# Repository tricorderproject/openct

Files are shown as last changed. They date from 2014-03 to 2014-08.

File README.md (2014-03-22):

openct
======

Open Source Computed Tomography (CT) Scanner <br>
http://www.tricorderproject.org/openct <br>
Copyright (C) 2014  Peter Jansen and the Tricorder project <br>
peter@tricorderproject.org <br>

*Early alpha release v0.1*

# Introduction

The Open Source Computed Tomography (CT) Scanner project aims to move towards creating an inexpensive and open desktop computed tomography scanner for academic and educational purposes.  The most common form of computed tomography is radiographic using x-rays or gamma rays, although it is my hope that this project can serve as a general platform for other kinds of tomographic research with other, safer wavelengths. 

This project is intended for use with radioisotope "check" sources that are many orders of magnitude less intense than sources in a commercial or medical radiographic setups.  This means that even very low resolution images will take hours of measurement and integration time to assemble, and the resolution and signal to noise ratio of a scan are largely a function of time (and patience).  Much of the spirit of this project is to move towards creating better scans through the use of clever signal processing techniques or wavelengths that can be more efficiently detected, rather than increasing source intensity. 

# Open Source

This project is open hardware and is released under various open licenses.  Please see LICENSES.TXT for details.

For potential contributors, a list of suggested contributions and next steps can be found in TODO.TXT .

# Warning

This project has a variety of dangers associated with it, including (without limitation) its assembly and use.  This generally includes the typical hazards involved with assembling, testing, and using electronics projects, CNC projects, as well as using hand tools, power tools, and CNC manufacturing tools such as laser cutters or CNC routers.  This is not a first project in any of these areas, and one should be well experienced and comfortable in all aspects of this project's design, assembly, and use. 

In addition, for radiography this project makes use of a low intensity sealed radioactive radioisotope source.  You should be experienced and extremely comfortable with handling and using radioactive sources, understanding the potential dangers (and how to minimize them), as well as any local laws or regulations regarding such material.  Having advanced training in medical imaging, radiography, and/or radiation biophysics is highly recommended.  

In no case should any living thing be placed inside of or be scanned by the device. 

**DISCLAIMER OF WARRANTIES AND LIMITATION OF LIABILITY.**

UNLESS OTHERWISE SEPARATELY UNDERTAKEN BY THE LICENSOR, TO THE EXTENT POSSIBLE, THE LICENSOR OFFERS THE LICENSED MATERIAL AS-IS AND AS-AVAILABLE, AND MAKES NO REPRESENTATIONS OR WARRANTIES OF ANY KIND CONCERNING THE LICENSED MATERIAL, WHETHER EXPRESS, IMPLIED, STATUTORY, OR OTHER. THIS INCLUDES, WITHOUT LIMITATION, WARRANTIES OF TITLE, MERCHANTABILITY, FITNESS FOR A PARTICULAR PURPOSE, NON-INFRINGEMENT, ABSENCE OF LATENT OR OTHER DEFECTS, ACCURACY, OR THE PRESENCE OR ABSENCE OF ERRORS, WHETHER OR NOT KNOWN OR DISCOVERABLE. WHERE DISCLAIMERS OF WARRANTIES ARE NOT ALLOWED IN FULL OR IN PART, THIS DISCLAIMER MAY NOT APPLY TO YOU.

TO THE EXTENT POSSIBLE, IN NO EVENT WILL THE LICENSOR BE LIABLE TO YOU ON ANY LEGAL THEORY (INCLUDING, WITHOUT LIMITATION, NEGLIGENCE) OR OTHERWISE FOR ANY DIRECT, SPECIAL, INDIRECT, INCIDENTAL, CONSEQUENTIAL, PUNITIVE, EXEMPLARY, OR OTHER LOSSES, COSTS, EXPENSES, OR DAMAGES ARISING OUT OF THIS PUBLIC LICENSE OR USE OF THE LICENSED MATERIAL, EVEN IF THE LICENSOR HAS BEEN ADVISED OF THE POSSIBILITY OF SUCH LOSSES, COSTS, EXPENSES, OR DAMAGES. WHERE A LIMITATION OF LIABILITY IS NOT ALLOWED IN FULL OR IN PART, THIS LIMITATION MAY NOT APPLY TO YOU.

THE DISCLAIMER OF WARRANTIES AND LIMITATION OF LIABILITY PROVIDED ABOVE SHALL BE INTERPRETED IN A MANNER THAT, TO THE EXTENT POSSIBLE, MOST CLOSELY APPROXIMATES AN ABSOLUTE DISCLAIMER AND WAIVER OF ALL LIABILITY.

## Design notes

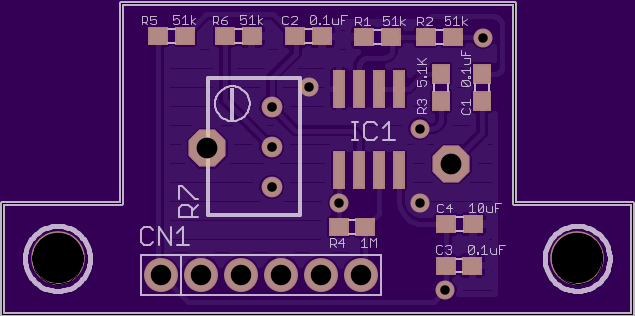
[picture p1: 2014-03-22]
pcb/external_comparator/type5comparator_top.png

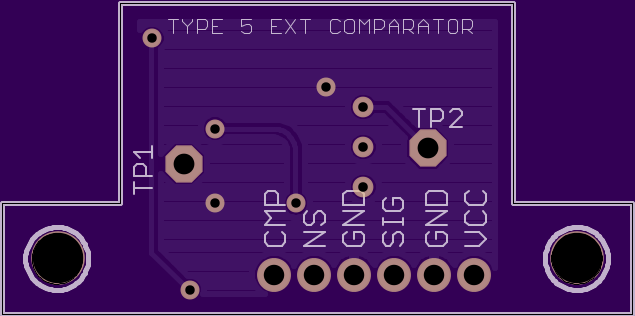
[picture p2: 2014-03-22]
pcb/external_comparator/type5comparator_bottom.png

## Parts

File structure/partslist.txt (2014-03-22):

========================
	GENERAL
========================

- T-slot captive nut holes are generally for 6/32 machine screws, 1/2 inch length. 
  A box of 100x 6/32 size 1/2 inch length bolts, nuts, and washers should suffice
  for most of the structural components.  A handful of longer lengths are required
  for the linear axis end plates and the carriage mounts. 

========================
	TABLE
========================

- MOTOR: NEMA14 5mm shaft [QTY: 1]
(Recommended: Japan Servo Co. Ltd. KP35FM2-035 from Sayal Electronics) 
(http://www.sayal.com)

- SCREW: M8 Nylon Screw and Nut.  [QTY: 1]
(Recommended: McMaster-Carr #98882A800, #93800A154)

- COUPLER: M5 to M8 Flex coupler
(Recommended: http://www.adafruit.com/products/1176 )

========================
	LINEAR AXES
========================

- MOTOR: NEMA14 5mm shaft [QTY: 2]
(Recommended: Japan Servo Co. Ltd. KP35FM2-035 from Sayal Electronics)

- BELT: At least 4 feet of 6mm width MLX (2.03mm pitch) belt.
(Recommended: Trim down SDP/SI (sdp-si.com) #A 6Z16MB89060 [QTY: 1])

- TIMING PULLEYS: SDP/SI (sdp-si.com) #A 6T16M018DF6005 [QTY: 2]

- IDLER PULLEYS: Makerslide Smooth Idler Wheel Kit [QTY: 2]
https://www.inventables.com/technologies/smooth-idler-wheel-kit
Also requires M5 bolts and lock nuts

- BUSHING: 1/4 Inner-diameter, 3/8 Outer-diameter snap bushing [QTY: 8]
(Recommended: from ACE Hardware)

- RODS: 1/4 aluminum rods, approx. 6 inches. [QTY: 4]
(Recommended: Cut from two 12 inch aluminum rods)

========================
	ROTATIONAL AXIS
========================

- MOTOR: NEMA17 5mm shaft [QTY: 1]
( Recommended: Adafruit http://www.adafruit.com/products/324 )

- BELT: SDP/SI (sdp-si.com) #A 6B16-115025 [QTY: 1]

- TIMING PULLEY: SDP/SI (sdp-si.com) #A 6T16M022DF6005 [QTY: 1]

========================
	BASE
========================

- BUSHING: 1/4 Inner-diameter, XX Outer-diameter, with flange
(Recommended: from ACE Hardware)

- RODS: 1/4 inch rods for timing gears, approx. 4 inches (cut to size) [QTY: 2]
(Recommended: Cut from one 12 inch aluminum rod)

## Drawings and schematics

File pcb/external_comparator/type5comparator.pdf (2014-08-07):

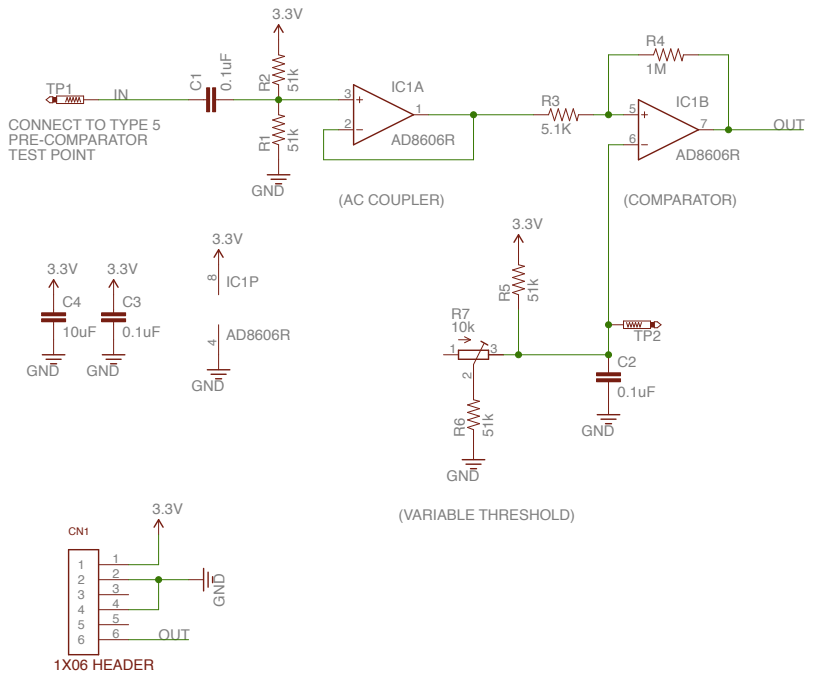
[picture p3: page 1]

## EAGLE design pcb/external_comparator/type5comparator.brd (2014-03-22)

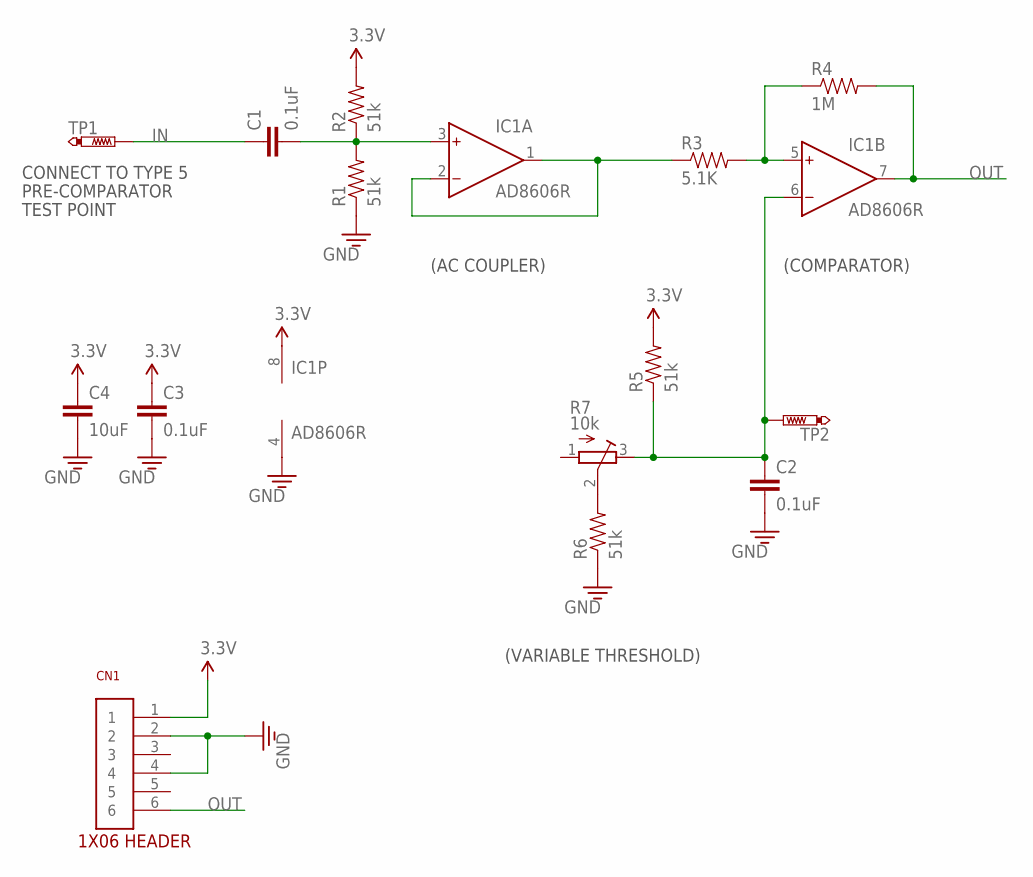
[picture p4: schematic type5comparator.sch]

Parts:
C1, C2, C3: 0.1uF; 0603
C4: 10uF; 0603
CN1: 1X06
IC1: AD8606R; SO8
R1, R2, R5, R6: 51k; 0603
R3: 5.1K; 0603
R4: 1M; 0603
R7: 10k; RTRIM3299W
TP1, TP2: PTR1PAD1-13; P1-13

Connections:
3.3V: C3.1, C4.1, CN1.1, IC1.8 (V+), R2.2, R5.2
GND: C2.2, C3.2, C4.2, CN1.2, CN1.4, IC1.4 (V-), R1.1, R6.1
IN: C1.1, TP1.TP
unnamed: R6.2, R7.2 (S)
unnamed: C1.2, IC1.3 (IN+), R1.2, R2.1
unnamed: IC1.1 (OUT), IC1.2 (IN-), R3.1
unnamed: IC1.5 (IN+), R3.2, R4.1
unnamed: C2.1, IC1.6 (IN-), R5.1, R7.3 (A), TP2.TP
OUT: CN1.6, IC1.7 (OUT), R4.2

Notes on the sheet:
(AC COUPLER)
(COMPARATOR)
(VARIABLE THRESHOLD)
CONNECT TO TYPE 5
PRE-COMPARATOR
TEST POINT

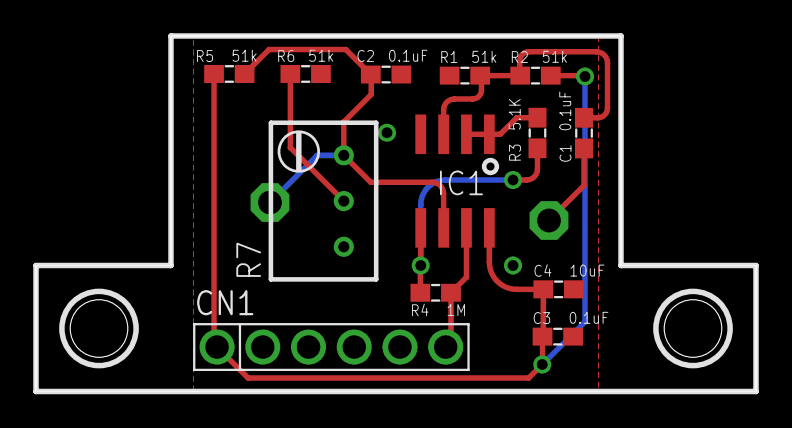
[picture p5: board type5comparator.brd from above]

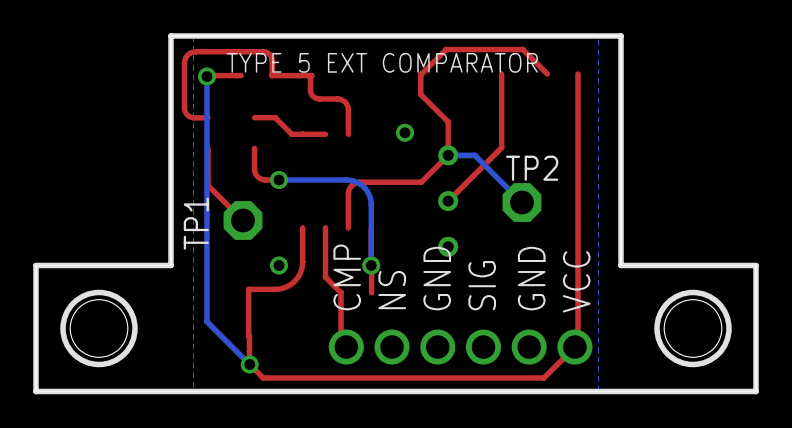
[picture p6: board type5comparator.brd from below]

Board: 2 copper layers, 40.0 x 19.8 mm, 15 parts (2 on the bottom side), 9 nets.

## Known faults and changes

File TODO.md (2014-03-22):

TODO LIST
======

Open Source Computed Tomography (CT) Scanner <br>
http://www.tricorderproject.org/openct <br>
Copyright (C) 2014  Peter Jansen and the Tricorder project <br>
peter@tricorderproject.org <br>

One of the most common questions an organizer of an open source project receives is, "How can I help?".  This TODO list outlines some of the near-term contributions that can be made to the project in a variety of categories, varying from simple to challenging. 

# Structural and Mechanical

- *End-stops:* Add end-stops ("limit switches") to each of the two linear axes, table axis, and rotational axis. 

- *Cabling:* Find a better solution to cable routing.  Cable routing is currently an issue, and there are a number of cables and signals that have to move from the rotating bore to the controller/arduino shield on the stationary base.  The rotational axis has to have at least 180&deg; of rotation, meaning that at one extreme it has a lot of slack, and at the other it has zero slack.  

- *Cabling, Part 2:* Is cabling the answer?  Should we turn the bore into a giant slip ring with two lines (+5V, GND) so that it can freely rotate 360&deg;, and wirelessly communicate between the bore and base using (for example) bluetooth? 

# Electronics

- *Arduino Shield:* Lay out an Arduino shield, for the latest Uno revision, that includes: (1) 4 Pololu stepper controllers (3 @ 5V, one selectable between 5V and 12V for the larger rotary axis stepper), (2) an SD/uSD socket for data storage, and (3) Headers/connectors for the end-stops, and an I2C accelerometer for sensing the rotational angle of the bore.  This should be compact enough to fit and mount inside one side of the base, and expose any required ports or connectors on the Arduino/Shield using clean cutouts in the back of the base. 

- *Rotational Sensing:* Currently the plan is to use an I2C accelerometer mounted in the bore as an absolute rotational sensor to sense the current angle of the bore.  Create the board for this, and add the supporting code into to the Arduino sketch.  A sensible place for this might be a tiny board that securely mounts on the back of the carriages and combines an accelerometer and two limit switches.  

# Source and Detector

- *Parallel Detector:* The current source/detector system is basically a working model of the first generation of CT scanner, that makes use of a single source and detector that are linearly scanned across the sample.  Modern systems speed this up dramatically by parallelizing the problem and using an large array of detectors in place of a single detector -- removing the need for linear scanning stages inside the bore, and reducing scan time by measuring all points for a given angle simultaneously.  This is a fairly large undertaking, and would likely require developing a custom parallel detector array with tens of detectors as inexpensively as possible.  

- *Alternate Sources/Detectors:* Using your advanced knowledge of optics, develop alternate source/detector pairs that examine different, safer wavelengths that objects of interest tend to be semi-transparent at.  (possible examples: Terahertz? Radio waves? Infrared?)

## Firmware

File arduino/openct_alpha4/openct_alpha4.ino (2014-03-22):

/*
  Open Source Computed Tomography (CT) Scanner 
  Demonstration code -- Early release alpha state

  This code is intended to demonstrate the basic functionality of the Open Source CT scanner, and 
  verify the basic functionality of the motion and detction system. 
  
  This code is intended for pairing with:
  1) An Arduino Uno R3
  2) A shield containing at least 3 (but preferably 4) Pololu stepper drivers
  3) A shield containing an SD card socket for data storage (the data is also mirrored over the serial console)
  4) A Radiation Watch Type 5 high energy particle detector modified with the external high-sensitivity comparator board
  5) The Open Source CT 4-axis motion system
  
  This code is in an prototype alpha state, and is intended for demonstration purposes only.  
  Portions of this file are from the Radiation Watch Type 5 Arduino example code.  All 
  other portions are released under the GPL V3 license. 
  
  TODO: 
  - Add 4 axis control as soon as the official 4-axis stepper shield is complete 
    (currently my prototype shield only has room for 3 stepper controllers, so either the table or rotational axis is disabled)
  - Add end-stop support for homing all axes
  - Add accelerometer for absolute angle sensing for rotational axis
  
 */
 
#include <SPI.h>
#include <SD.h>
const int SD_CS  = 10;    // Chip select pin of SD card
 
int TYPE5_DETECTOR = 2;   // High-sensitivity signal pin of detector from external comparator

// Stepper controller pinouts
int STEPPER_SLEEP = A0;   // Enable/disable pin for stepper controller
int STEP1   = 5;
int DIR1    = 4;
int STEP2   = 6;
int DIR2    = 7;
int STEP3   = 8;
int DIR3    = 9;

// Motion Parameters
int CHANNEL_SOURCE   = 3;
int CHANNEL_DETECTOR = 2;
int CHANNEL_TABLE    = 1;
int CHANNEL_ROTATION = 4;

int travel_max_srcdet   = 2500;
int travel_max_table    = 5000;

int SOURCE_UP     = 1;
int SOURCE_DOWN   = 0;
int DETECTOR_UP   = 1;
int DETECTOR_DOWN = 0;
int TABLE_IN      = 0;
int TABLE_OUT     = 1;

// Location information
int stepper_locations[4];

// scan information
int start_linear = 0;
int end_linear = 60;
int res_linear = 5;

int start_table = 0;
int end_table = 120;
int res_table = 5;

int integrationTime = 30;      // integration time, in seconds
int detector_offset = 2;       // detector offset, in millimeters 


// STEPPER FUNCTIONS
void stepper_enable(int mode) {
  // mode = 1 enables the stepper drivers, mode = 0 disables them
  if (mode == 1) {
    // enable
    digitalWrite(STEPPER_SLEEP, HIGH);    
  } else {
    digitalWrite(STEPPER_SLEEP, LOW);
  }
}


void stepper_move(int channel, int dir, int num_steps) {
  // Step motor 'channel' one step in direction 'dir'
  int i=0;
  int step_delay = 2000;    // in microseconds
  
  if (channel == CHANNEL_TABLE) {
    // Setup direction
    if (dir == 0) {
          digitalWrite(DIR1, LOW);    
    } else {
          digitalWrite(DIR1, HIGH);    
    }
    
    for (i=0; i<num_steps; i++) {
      // Step one step
      digitalWrite(STEP1, LOW);    
      digitalWrite(STEP1, HIGH);
      delayMicroseconds(step_delay); 
      digitalWrite(STEP1, LOW);   
      delayMicroseconds(step_delay);       
    }
    
  } else if (channel == CHANNEL_DETECTOR) {
    // Setup direction
    if (dir == 0) {
          digitalWrite(DIR2, LOW);    
    } else {
          digitalWrite(DIR2, HIGH);    
    }
    
    for (i=0; i<num_steps; i++) {
      // Step one step
      digitalWrite(STEP2, LOW);    
      digitalWrite(STEP2, HIGH);
      delayMicroseconds(step_delay); 
      digitalWrite(STEP2, LOW);
      delayMicroseconds(step_delay);     
    }
    
  } else if (channel == CHANNEL_SOURCE) {
    // Setup direction
    if (dir == 0) {
          digitalWrite(DIR3, LOW);    
    } else {
          digitalWrite(DIR3, HIGH);    
    }
    
    for (i=0; i<num_steps; i++) {
      // Step one step
      digitalWrite(STEP3, LOW);    
      digitalWrite(STEP3, HIGH);
      delayMicroseconds(step_delay); 
      digitalWrite(STEP3, LOW);    
      delayMicroseconds(step_delay);       
    }
  }      
  
}


void stepper_move_absolute(int channel, int distance) {
  int travel_per_mm_linear = 20;
  int travel_per_mm_table = 600;
  int delta = distance - stepper_locations[channel];
  
  if (channel == CHANNEL_TABLE) {
    delta = delta * travel_per_mm_table;
    if (delta < 0) {
      stepper_move(channel, TABLE_OUT, -delta);
    } else { 
      stepper_move(channel, TABLE_IN, delta);
    }        
  } else if (channel == CHANNEL_DETECTOR) {
    delta = delta * travel_per_mm_linear;
    if (delta < 0) {
      stepper_move(channel, DETECTOR_DOWN, -delta);
    } else { 
      stepper_move(channel, DETECTOR_UP, delta);
    }
  } else if (channel == CHANNEL_SOURCE) {
    delta = delta * travel_per_mm_linear;
    if (delta < 0) {
      stepper_move(channel, SOURCE_DOWN, -delta);
    } else { 
      stepper_move(channel, SOURCE_UP, delta);
    }    
  }
  stepper_locations[channel] = distance;
    
}

void init_stepper_positioning() {
  stepper_enable (1);
  stepper_move (CHANNEL_SOURCE, SOURCE_DOWN, travel_max_srcdet);
  stepper_move (CHANNEL_DETECTOR, DETECTOR_DOWN, travel_max_srcdet);
  
  // Initialize absolute position information
  stepper_locations[0] = 0;
  stepper_locations[1] = 0;
  stepper_locations[2] = 0;
  stepper_locations[3] = 0;
}



void scan_source_detector() {
  // Scans the source and detector from the top to the bottom, then moves them back to the top
  
  // Step 1: Move the source and detector to the start position
  stepper_enable (1);
  stepper_move_absolute(CHANNEL_SOURCE, 0);
  stepper_move_absolute(CHANNEL_DETECTOR, 0);  
//  stepper_enable (0);
      
  int i=0;
  for (i=start_linear; i<end_linear; i+= res_linear) {
    
    int y_position = i; // in millimeters
        
    stepper_enable (1);    
    stepper_move_absolute (CHANNEL_SOURCE, y_position);
    stepper_move_absolute (CHANNEL_DETECTOR, y_position + detector_offset); 

    // wait briefly for vibrations to stop
    delay(500);

    // take measurement
    int measurement = read_type5(integrationTime);
    double cpm = (double)measurement * (60.0f / (double)integrationTime);
    
    String csv = "";
    csv += stepper_locations[CHANNEL_SOURCE];
    csv += ",";
    csv += stepper_locations[CHANNEL_TABLE];
    csv += ",";
    csv += measurement;
    csv += ",";
    csv += cpm;
    
    Serial.println(csv);
    SD_writeline(csv);
    
  }
  
  stepper_enable (0);
  //stepper_move(ch, dir, steps);
}


int read_type5(int maxSeconds) {
  // This code is adapted from the Radiation Watch Type 5 Arduino example
  
  int totalSec=0;     // Elapsed time of measurement [sec]
  int totalHour=0;    // Elapsed time of measurement [hour]

  //Time settings for CPM calcuaration
  int cpmTimeMSec=0;
  int cpmTimeSec=0;
  int cpmTimeMin=0;
  
  int startTime = millis();
  int index = 0;

  int signCount=0;  //Counter for Radiation Pulse

  int sON=0;//Lock flag for Radiation Pulse
  int nON=0;//Lock flag for Noise Puls  
  
  while (totalSec < maxSeconds) {
    
    // Raw data of Radiation Pulse: Not-detected -> High, Detected -> Low
    int sign = digitalRead(TYPE5_DETECTOR);
  
    //### Output from external comparator is inverted from normal Type 5 output (high is detected)
    if (sign == 1) {
     sign = 0;
    } else {
     sign = 1;
    }

    // Radiation Pulse normally keeps low for about 100[usec]
    if(sign==0 && sON==0) { // Deactivate Radiation Pulse counting for a while
      sON = 1;
      signCount++;
    } else if(sign==1 && sON==1){
      sON = 0;
    }

    index += 1;
    if (index == 10000) {
      int currTime = millis();
      cpmTimeMSec += abs(currTime - startTime);
      if(cpmTimeMSec >= 1000) {
        cpmTimeMSec -= 1000;
        //Add measurement time to calcurate cpm readings (max=20min.)
        if( cpmTimeSec >= 20*60 ) {
          cpmTimeSec = 20*60;
        } else {
          cpmTimeSec++;
        }
        
        //Total measurement time
        totalSec++;
      }
    }

  }
  
  return signCount;
}

void SD_writeline (String text) {
  File fp = SD.open("data.txt", FILE_WRITE);
  fp.println(text);
  fp.flush();
  fp.close(); 
}

// the setup routine runs once when you press reset:
void setup() {           
  delay(1000);      // Give a moment to open the serial console
  
  // Open the serial port
  Serial.begin(9600);
  Serial.println ("Initializing...");
  
  // sleep pin for stepper drivers
  pinMode(STEPPER_SLEEP, OUTPUT);     
  
  // step/direction control for stepper drivers
  pinMode(DIR1, OUTPUT);     
  pinMode(STEP1, OUTPUT);     
  pinMode(DIR2, OUTPUT);     
  pinMode(STEP2, OUTPUT);     
  pinMode(DIR3, OUTPUT);     
  pinMode(STEP3, OUTPUT);     
  
  // SD card
  Serial.print("Initializing SD card...");
  pinMode(SD_CS, OUTPUT);
  if (!SD.begin(SD_CS)) {
    Serial.println("ERROR: SD card failed, or not present");
    return;
  }
  Serial.println("SD card initialized...");
  SD_writeline("----------");
  
  
  // Enable the stepper drivers
  stepper_enable(1);  
  init_stepper_positioning();
  
  // Display prompt to user
  delay(2000);
  Serial.println ("Format: linear,table,measurement,cpm");
  Serial.println ("Scanning... ");
  
  int z = 0;
  for (z=start_table; z<end_table; z+=res_table) {
    scan_source_detector();
    stepper_enable (1);
    stepper_move_absolute(CHANNEL_TABLE, z);
    stepper_enable (0);
    delay(500);
  }
  
  stepper_move_absolute(CHANNEL_TABLE, 0);
  Serial.println ("");
  Serial.println ("Scan complete...");
  return;

}


void loop() {
  while(1) {
    // do nothing
  }
}
